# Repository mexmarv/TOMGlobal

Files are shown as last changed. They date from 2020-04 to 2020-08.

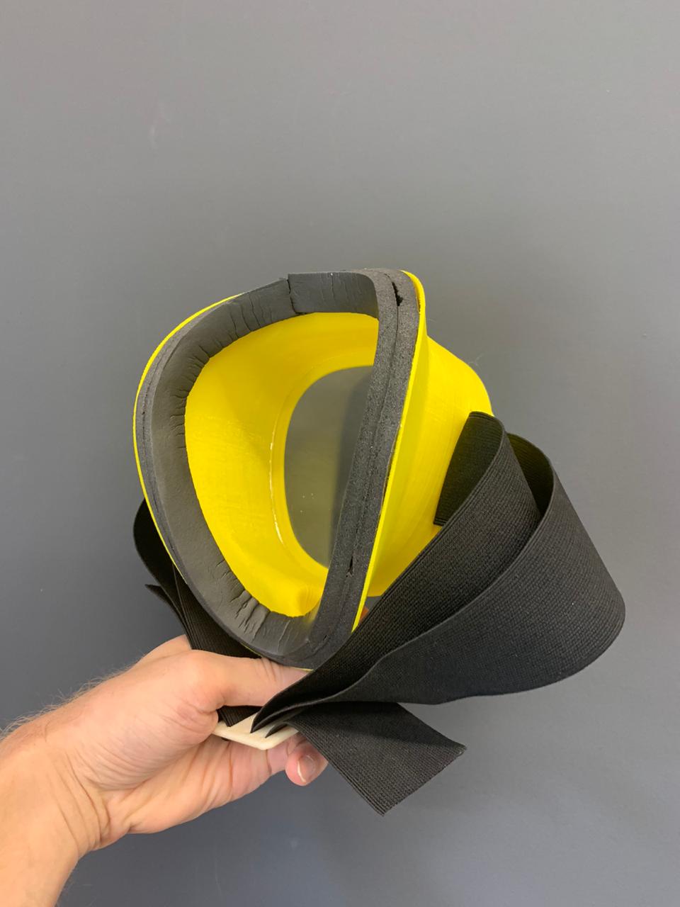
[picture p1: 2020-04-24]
UNO/photos/3.jpeg

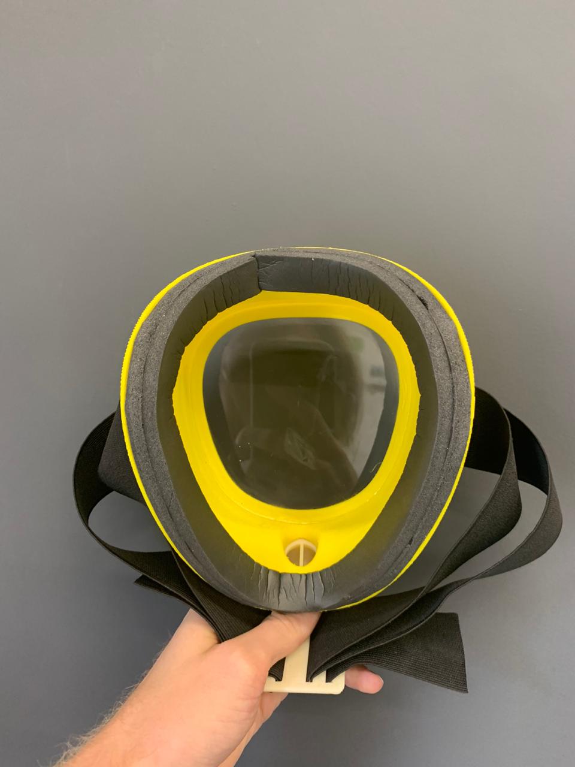
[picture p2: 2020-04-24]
UNO/photos/2.jpeg

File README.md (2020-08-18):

# TOM Global - México Chapter
</br>
<a target="TOM" href="www.makersmexico.org">makersmexico.org</a>

Encuentra todos los archivos de 3D y software que contribuimos de la comunidad que encuentras en makersmexico.org.

## Instalación:
```bash
git clone https://github.com/mexmarv/TOMGlobal.git
cd TOMGlobal
cd .. (UNO | mascaras | splitters | ventiladores)
```
## UNO - Máscara Paciente por ARDS
<li>PEEP-Valve-ARDS_es</li>
<li>UNO *.stl</li>

## mascaras
<li>SitresClips</li>
<li>Stratasys-Letter</li>

## ventiladores
<li>VentMex</li>

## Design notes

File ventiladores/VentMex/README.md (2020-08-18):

# VentMex : Ventilador de Emergencia
</br>
<a target="TOM" href="www.makersmexico.org">makersmexico.org/ventmex</a>

Puedes ver el sitio del proyecto directamente para explicación de todo el proyecto.

## Instalación:
```bash
git clone https://github.com/mexmarv/TOMGlobal.git
cd TOMGlobal/ventiladores/VentMex
cd .. ( VM2.1 | VM-SensorTest | VM-MotorTest | STL | gerber | otros )
```
## VM2.1
<ul>
<li>Software y Libs de Arduino para VentMex
<ul>
<li> Se incluye Librería de encoder del AMS-AS5048B, Nuestras Librerías: VMPresion.h, VMFlujo.h, VMConstantes.h 
</li>
</ul>
</li>
<li>Librerías necesarias que se deben de instalar son:
<ul>
<li>
 AccelStepper (Última Version)
</li>
<li>
 U8g2 (Última Versión)
 </li>
 <li>
SparkFun MAX30101x  (Última Versión)
</li>
</ul>
</ul>

## stl
<li>Archvos Imprimibles de VentMex 2.1 formato .STL</li>
<li>Recomendamos impresión con 80% infill y soportes donde sea necsario</li>

## gerber
<li>Archvos para hacer tu propio VentMex 2.0 Shield para Arduino Mega.</li>

## otros
<li>BOM (Bill of Materials - Lista de Materiales), Cálculo de Volúmen Comandado a pasos, y otros.</li>
<li>Varios</li>

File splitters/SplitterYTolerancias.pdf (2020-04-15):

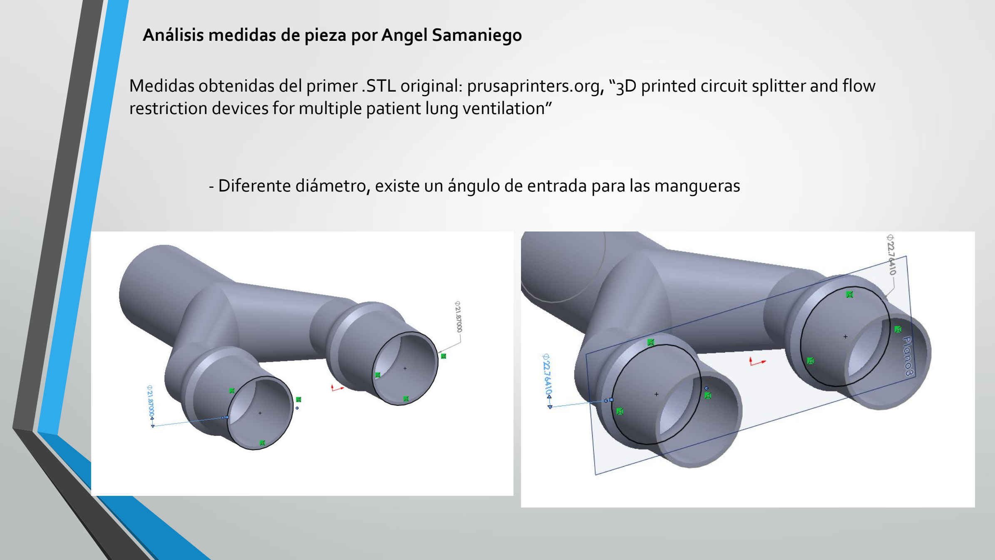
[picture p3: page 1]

Medidas obtenidas del primer .STL original: prusaprinters.org, “3D printed circuit splitter and flow restriction devices for multiple patient lung ventilation”

Análisis medidas de pieza por Angel Samaniego

- Diferente diámetro, existe un ángulo de entrada para las mangueras

Medidas obtenidas del primer STL original:

- Diferente diámetro, existe un Angulo de entrada para las mangueras

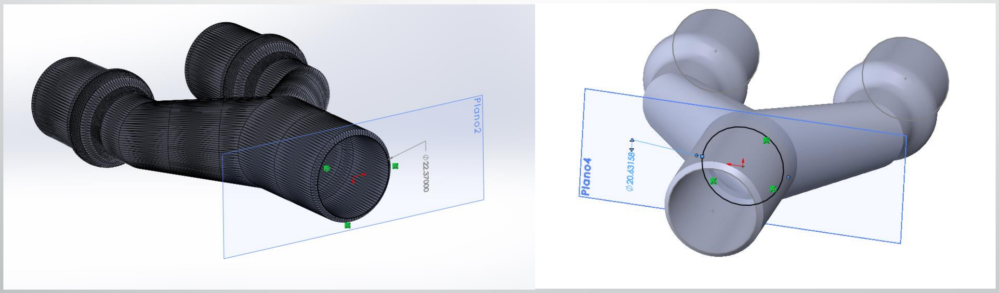
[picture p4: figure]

Tamaño Correcto 22.37 mm

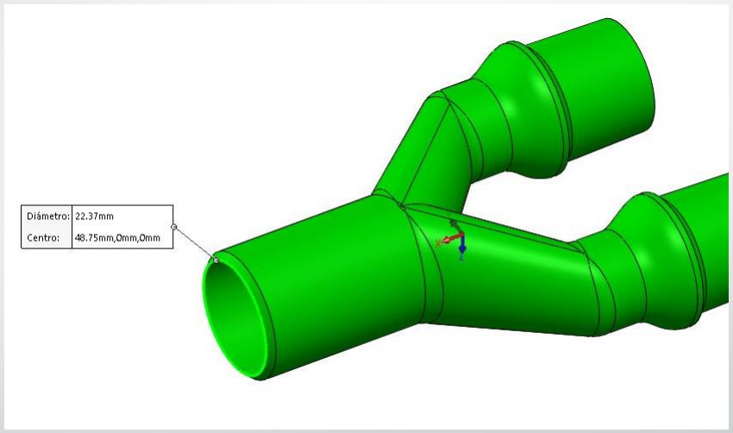
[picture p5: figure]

Tamaño Correcto 21.87 mm

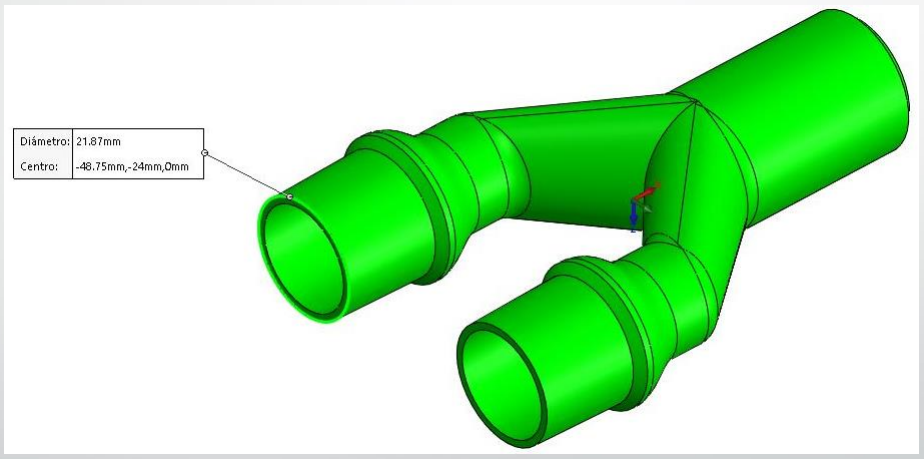
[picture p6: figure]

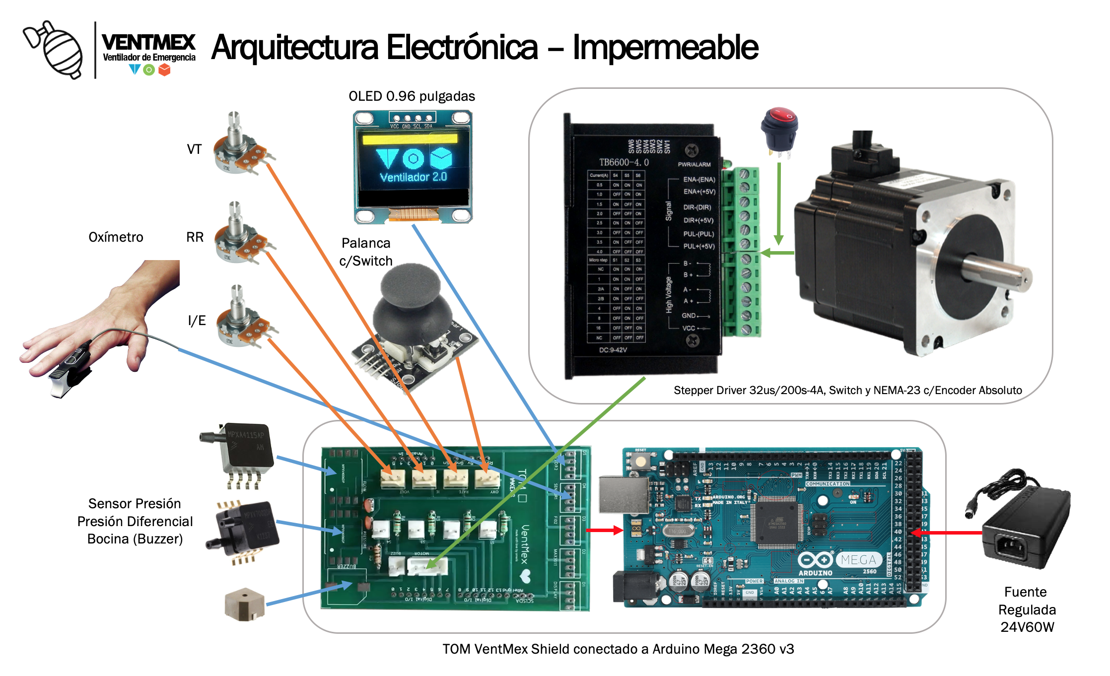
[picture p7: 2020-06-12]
ventiladores/VentMex/otros/VM_DiagElec-figs.png

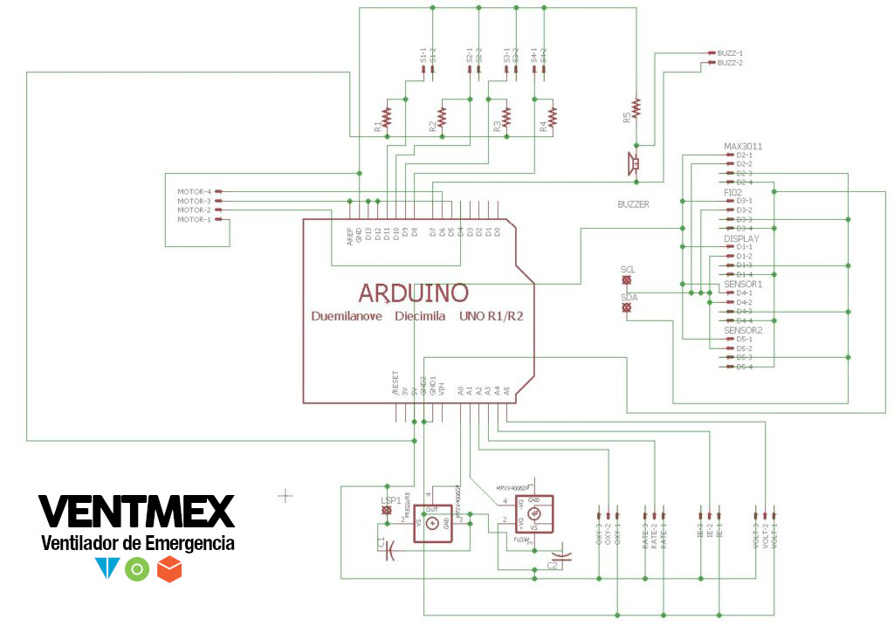
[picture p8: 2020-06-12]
ventiladores/VentMex/otros/VM_DiagElec-schem.jpg

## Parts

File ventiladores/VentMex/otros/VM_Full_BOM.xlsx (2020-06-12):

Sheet: Sheet 1 - VentCore
VentMex - BOM (Bill of Materials) |  |  |  |  |  | Tipo de Cambio | $22.50 | $7889.57
Ca | Familia | Valor | Parte | Paquete | Piezas | Precio USD | Precio MXN | Importe MXN | Comentarios | Imagen
1 | ELECTRONICO | AUDIO MAGNETIC XDCR 3-7V SMD | BUZZER | BUZZ | BUZZ | $1.54 | $34.65 | $34.65
1 | ELECTRONICO | MPXV4006DP | MPXV4006DP | SOP8 | SN1 | $19.55 | $439.88 | $439.88
1 | ELECTRONICO | MPXV4006GP | MPXV4006GP | SOP8 | SN3 | $19.55 | $439.88 | $439.88
5 | ELECTRONICO |  | Resistencia 10k |  | R1, R2, R3, R4 ,R5 | $0.05 | $1.12 | $5.62
2 | ELECTRONICO |  | Resistencia 90 ohms |  | R6 R7 | $0.05 | $1.12 | $2.25
2 | ELECTRONICO |  | Capacitor Ceramico 100 uF |  | C1 y C2 | $0.07 | $1.69 | $3.38
1 | ELECTRONICO |  | Arduino Mega |  |  | $11.11 | $250.00 | $250.00
1 | ELECTRONICO |  | 12V 60W AC/DC Fuente de alimentación |  |  | $20.00 | $450.00 | $450.00
1 | ELECTRONICO |  | Stepper motor Nema-23P |  |  | $38.69 | $870.52 | $870.52
1 | ELECTRONICO |  | Driver TB660 4 A |  |  | $20.89 | $470.00 | $470.00
1 | ELECTRONICO |  | VentMex Shield |  |  | $3.56 | $80.00 | $80.00
3 | ELECTRONICO |  | Potentiometer |  |  | $0.44 | $10.00 | $30.00 | 10 K
1 | ELECTRONICO |  | Conector 12v IP67 |  |  | $9.00 | $202.50 | $202.50
1 | ELECTRONICO |  | SWITCH IP67 |  |  | $2.00 | $45.00 | $45.00
1 | ELECTRONICO |  | Conector USB IP67 para programador |  |  | $15.00 | $337.50 | $337.50
1 | ELECTRONICO |  | Encoder Magnetico |  |  | $16.00 | $360.00 | $360.00
1 | ELECTRONICO |  | Display |  |  | $5.73 | $129.00 | $129.00
1 | ELECTRONICO |  | Oximetro Max30102 |  |  | $10.67 | $240.00 | $240.00
1 | ELECTRONICO |  | Joystick Arduino c/botón |  | Mercado libre | $5.73 | $129.00 | $129.00
1 | MECANICO |  | O_belt |  |  | $1.60 | $36.00 | $36.00
 | MECANICO |  | Baleros 6 |  | MercadoLibre | $2.22 | $50.00 | $50.00
1 | MECANICO | alucobond_file | CNC_bottom |  |  | $15.91 | $358.00 | $358.00 | http://www.dimmaq.com/
1 | MECANICO | sheetmetal_files | SM_internal |  |  | $13.11 | $295.00 | $295.00 | http://www.dimmaq.com/
1 | MECANICO | acrylic_files | CNC_back |  |  | $5.69 | $128.00 | $128.00 | http://www.dimmaq.com/
1 | MECANICO | acrylic_files | CNC_front |  |  | $5.69 | $128.00 | $128.00 | http://www.dimmaq.com/
1 | MECANICO | sheetmetal_files | SM_external |  |  | $10.00 | $225.00 | $225.00 | http://www.dimmaq.com/
1 | MEDICO | Dispositivo de ventilación Bolsa-Válvula-Mascara BVM | BVM v1 |  |  | $31.73 | $714.00 | $714.00
1 | MEDICO |  | Circuito Ventilador Medico 2 Trampas De Agua 1.5m |  | Peso(g) | $26.67 | $600.00 | $600.00 | Mercado Libre (https://articulo.mercadolibre.com.mx/MLM-766206422-circuito-ventilador-medico-2-trampas-de-agua-15m-_JM?quantity=1)
3 | IMPRESION 3D | STL_files | 3PD_spin(rodillo) | Relleno 50%, espesor de capa 0.15 | 45 | $1.20 | $27.00 | $81.00 | Talla 30 x 30 x 50 Volumen ( mm 3 ) 33,677
1 | IMPRESION 3D | STL_files | 3DP_bvmholder_2aP(soporte ambu) | Relleno 100%, espesor de capa 0.15 | 31 | $0.83 | $18.60 | $18.60 | Talla 8 x 88 x 61 Volumen ( mm 3 ) 24,004
3 | IMPRESION 3D | STL_files | 3DP_knobs(potencionmetros) | Relleno 100%, espesor de capa 0.15 | 4 | $0.11 | $2.40 | $7.20 | Talla 18 x 15 x 18 Volumen ( mm 3 ) 2,045
2 | IMPRESION 3D | STL_files | 3DP_pcbholder | Relleno 50%, espesor de capa 0.15 | 2 | $0.05 | $1.20 | $2.40 | Talla 10 x 4 x 35 Volumen ( mm 3 ) 868
1 | IMPRESION 3D | STL_files | 3PD_arc_1 (Bolsa Ambu Bag) | Relleno 35%, espesor de capa 0.15 | 218 | $5.81 | $130.80 | $130.80 | Talla 120 x 40 x 110 Volumen ( mm 3 ) 305,245
1 | IMPRESION 3D | STL_files | 3DP_bvmholder_1aP(soporte ambu) | Relleno 100%, espesor de capa 0.15 | 43 | $1.15 | $25.80 | $25.80 | Talla 8 x 94 x 85 Volumen ( mm 3 ) 33,079
1 | IMPRESION 3D | STL_files | 3DP_bvmholder_1bP(soporte ambu) | Relleno 100%, espesor de capa 0.15 | 22 | $0.59 | $13.20 | $13.20 | Talla 8 x 94 x 85 Volumen ( mm 3 ) 16,719
1 | IMPRESION 3D | STL_files | 3DP_bvmholder_2bP(soporte ambu) | Relleno 100%, espesor de capa 0.15 | 19 | $0.51 | $11.40 | $11.40 | Talla 8 x 88 x 61 Volumen ( mm 3 ) 14,783
1 | IMPRESION 3D | STL_files | 3DP_motor_3(motor) | Relleno 50%, espesor de capa 0.15 | 2 | $0.05 | $1.20 | $1.20 | Talla 5 x 30 x 30 Volumen ( mm 3 ) 1,510
1 | IMPRESION 3D | STL_files | 3DP_motor_1(rodillo ranurado) | Relleno 50%, espesor de capa 0.15 | 45 | $1.20 | $27.00 | $27.00 | Talla 40 x 40 x 59 Volumen ( mm 3 ) 57,388
1 | IMPRESION 3D | STL_files | 3DP_motor_2(motor) | Relleno 50%, espesor de capa 0.15 | 2 | $0.05 | $1.20 | $1.20 | Talla 6 x 33 x 15 Volumen ( mm 3 ) 1,178
3 | SUJECION |  | O_shoulderscrew |  |  | $3.55 | $79.88 | $239.62 | Tornillos de eje de rodamiento - con ranura de anillo de retención, Soporte Sspin Ø6mm (https://www.fastenal.com/)
3 | SUJECION |  | hex nut style 1 gradeab_iso_ISO - 4032 - M6 - D - N |  |  | $1.23 | $27.68 | $83.03 | https://www.fastenal.com/
4 | SUJECION |  | pan head cross recess screw_iso_ISO 7045 - M5 x 10 - Z - 10N |  |  | $0.19 | $4.28 | $17.10 | https://www.fastenal.com/
10 | SUJECION |  | pan head cross recess screw_iso_ISO 7045 - M3 x 10 - Z - 10N |  |  | $0.18 | $4.05 | $40.50 | https://www.fastenal.com/
12 | SUJECION |  | pan head cross recess screw_iso_ISO 7045 - M3 x 12 - Z - 12N |  |  | $0.27 | $6.08 | $72.90 | https://www.fastenal.com/
16 | SUJECION |  | hex nut style 1gradeab_iso_ISO - 4032 - M3 - D - N |  |  | $0.04 | $0.90 | $14.40 | https://www.fastenal.com/
14 | SUJECION |  | pan head cross recess screw_iso_ISO 7045 - M4 x 12 - Z - 12N |  |  | $0.11 | $2.48 | $34.65 | https://www.fastenal.com/
4 | SUJECION |  | hex nut style 1 gradeab_iso_ISO - 4032 - M5 - D - N |  |  | $0.16 | $3.60 | $14.40 | https://www.fastenal.com/

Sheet: Inventory
 |  |  |  |  |  |  | VentCore BOM |  |  | Tipo de Cambio | $24.12 | $7763.70
Qty | Imagen | DigiKey Part Number | Manufacturer Part Number | Description | Familia | Value | Device | Package | Parts | Precio USD | Precio MXN | Importe MXN | Comentarios | Quantity | DigiKey Part Number | Manufacturer Part Number | Description | Customer Reference | Available | Backorder | Unit Price | Extended Price USD
1 |  | 102-1266-1-ND | CT-1205H-SMT-TR | AUDIO MAGNETIC XDCR 3-7V SMD | ELECTRONIC |  | BUZZER | BUZZ | BUZZ | $1.54 | $37.14 | $37.14 |  | 1 | 102-1266-1-ND | CT-1205H-SMT-TR | AUDIO MAGNETIC XDCR 3-7V SMD | BUZZ | 1 | 0 | $1.54
1 |  | KPJX-4S-S | 2092-KPJX-4S-S-ND | CONN JACK FMALE 4POS SOLDADURA DE ESTAÑO | ELECTRONIC |  | KPJX-4S | KPJX-4S | J7 | $2.23 | $53.78 | $53.78 | Remplaza KPJX-4S-S a 2092-KPJX-4S-ND | 1 | KPJX-4S-S | 2092-KPJX-4S-S-ND | CONN JACK FMALE 4POS SOLDADURA DE ESTAÑO |  | 1 | 0 | $2.23
1 |  | 497-12404-ND | L7805CV-DG | IC REG LINEAR 5V 1.5A TO220 | ELECTRONIC |  | L7805CV-DG | TO220-IGO | IC2 | $0.57 | $13.75 | $13.75 |  | 1 | 497-12404-ND | L7805CV-DG | IC REG LINEAR 5V 1.5A TO220 |  | 1 | 0 | $0.57
2 |  | P.10AJCT-ND | ERJ-3RSFR10V | RES 0.1 OHM 1% 1/10W 0603 | ELECTRONIC | 0.1R | 0603 | R0603 | R14, R23 | $0.29 | $6.99 | $13.99 |  | 2 | P.10AJCT-ND | ERJ-3RSFR10V | RES 0.1 OHM 1% 1/10W 0603 |  | 2 | 0 | $0.29
1 |  | RHM100DCT-ND | ESR03EZPJ101 | RES SMD 100 OHM 5% 1/4W 0603 | ELECTRONIC | 100R | 0603 | R0603 | R7 | $0.10 | $2.41 | $2.41 |  | 1 | RHM100DCT-ND | ESR03EZPJ101 | RES SMD 100 OHM 5% 1/4W 0603 |  | 1 | 0 | $0.10
11 |  | 399-1100-1-ND | C0603C104Z3VACTU | CAP CER 0.1UF 25V Y5V 0603 | ELECTRONIC | 100nF | 0603 | C0603 | C17, C22, C25, C27, C33, C10, C11, C4, C5, C6, C8 | $0.03 | $0.77 | $8.49 | Faltan en BOM Ruben |  | 399-1100-1-ND | C0603C104Z3VACTU | CAP CER 0.1UF 25V Y5V 0603 |  | 11 | 0 | $0.03
6 |  | 718-1920-1-ND | TL8A0107M6R3C | Vishay Sprague | ELECTRONIC | 100uF | C-PR-SMD-SV-D | SV-D | C15 | $1.36 | $32.80 | $196.78 | Faltan en BOM Ruben |  | 718-1920-1-ND | TL8A0107M6R3C | Vishay Sprague | CAP TANT 100UF 20% 6.3V 1206 | 6 | 0 | $1.36
2 |  | 311-10KGRCT-ND | RC0603JR-0710KL | RES SMD 10K OHM 5% 1/10W 0603 | ELECTRONIC | 10K | 0603 | R0603 | R1, R4, R5, R6, R8, R21 | $0.19 | $4.58 | $9.16 |  | 10 | 311-10KGRCT-ND | RC0603JR-0710KL | RES SMD 10K OHM 5% 1/10W 0603 | R1, R4, R5, R6, R8, R21 | 10 | 0 | $19.00
6 |  | TC33X-103ECT-ND | TC33X-2-103E | TRIMMER 10K OHM 0.1W J LEAD TOP | ELECTRONIC | 10k | TRIMPOTTC33X | TC33X | VR1 | $0.28 | $6.75 | $40.51 |  | 1 | TC33X-103ECT-ND | TC33X-2-103E | TRIMMER 10K OHM 0.1W J LEAD TOP |  | 1 | 0 | $0.28
1 |  | 399-7842-1-ND | C0603C103M5RACTU | CAP CER 10000PF 50V X7R 0603 | ELECTRONIC | 10nF | 0603 | C0603 | C19 | $0.10 | $2.41 | $2.41 |  | 1 | 399-7842-1-ND | C0603C103M5RACTU | CAP CER 10000PF 50V X7R 0603 |  | 1 | 0 | $0.10
1 |  | 718-1124-1-ND | 293D106X9016B2TE3 | Vishay Sprague | ELECTRONIC | 10uF | C-PR-SMD-SV-B | SV-B | C16 | $0.44 | $10.61 | $10.61 | Faltan en BOM Ruben |  | 718-1124-1-ND | 293D106X9016B2TE3 | Vishay Sprague | CAP TANT 10UF 10% 16V 1411 | 6 | 0 | $0.44
1 |  | 399-4925-1-ND | C0805C106K8PACTU | CAP CER 10UF 10V X5R 0805 | ELECTRONIC | 10uf | 0805 | C0805 | C9 | $0.16 | $3.86 | $3.86 |  | 1 | 399-4925-1-ND | C0805C106K8PACTU | CAP CER 10UF 10V X5R 0805 |  | 1 | 0 | $0.16
1 |  | 311-120ARCT-ND | RC0805JR-07120RL | RES SMD 120 OHM 5% 1/8W 0805 | ELECTRONIC | 120R | 0805 | R0805 | R36 | $0.10 | $2.41 | $2.41 |  | 1 | 311-120ARCT-ND | RC0805JR-07120RL | RES SMD 120 OHM 5% 1/8W 0805 |  | 1 | 0 | $0.10
1 |  | 535-9875-1-ND | ABLS2-16.000MHZ-D4Y-T | CRYSTAL 16.0000MHZ 18PF SMD | ELECTRONIC | 16MHZ | DIP-CRYSTAL-16MHZ-18PF-30PPM-40R(HC49US) | HC49US | Y1 | $0.46 | $11.09 | $11.09 |  | 1 | 535-9875-1-ND | ABLS2-16.000MHZ-D4Y-T | CRYSTAL 16.0000MHZ 18PF SMD |  | 1 | 0 | $0.46
1 |  | 1N4004-TPMSCT-ND | 1N4004-TP | DIODE GEN PURP 400V 1A DO41 | ELECTRONIC | 1N4004 | 1N4004 | DO41-10 | D1 | $0.12 | $2.89 | $2.89 |  | 1 | 1N4004-TPMSCT-ND | 1N4004-TP | DIODE GEN PURP 400V 1A DO41 |  | 1 | 0 | $0.12
2 |  | 1276-6524-1-ND | CL10B105MO8NNWC | TAPA CER 1UF 16V X7R 0603 | ELECTRONIC | 1uf | 0603 | C0603 | C3, C7 | $0.10 | $2.41 | $4.82 | Review vs partida 19 399-3118-1-ND C0603C105K8PACTU | 2 | 1276-6524-1-ND | CL10B105MO8NNWC | TAPA CER 1UF 16V X7R 0603 | C3, C7 | 2 | 0 | $0.10
2 |  | 311-22.0HRCT-ND | RC0603FR-0722RL | RES SMD 22 OHM 1% 1/10W 0603 | ELECTRONIC | 22R | 0603 | R0603 | R2, R3 | $0.10 | $2.41 | $4.82 |  | 2 | 311-22.0HRCT-ND | RC0603FR-0722RL | RES SMD 22 OHM 1% 1/10W 0603 |  | 2 | 0 | $0.10
2 |  | 399-7874-1-ND | C0603C220J1GACTU | CAP CER 22PF 100V C0G/NP0 0603 | ELECTRONIC | 22pf | 0603 | C0603 | C1, C2 | $0.10 | $2.41 | $4.82 |  | 2 | 399-7874-1-ND | C0603C220J1GACTU | CAP CER 22PF 100V C0G/NP0 0603 |  | 2 | 0 | $0.10
1 |  | 311-3365-1-ND | CC0603KRX5R8BB474 | CAP CER 0.47UF 25V X5R 0603 | ELECTRONIC | 470nF | 0603 | C0603 | C23 | $0.18 | $4.34 | $4.34 |  | 1 | 311-3365-1-ND | CC0603KRX5R8BB474 | CAP CER 0.47UF 25V X5R 0603 |  | 1 | 0 | $0.18
1 |  | ATMEGA32U4-AU-ND | ATMEGA32U4-AU | IC MCU 8BIT 32KB FLASH 44TQFP | ELECTRONIC | ATMEGA32U4-TQFP44 | MCU-ATMEGA32U4-AU(TQFP44) | TQFP44-0.8-9.6X9.6MM | U1 | $4.00 | $96.46 | $96.46 |  | 1 | ATMEGA32U4-AU-ND | ATMEGA32U4-AU | IC MCU 8BIT 32KB FLASH 44TQFP | U1 | 1 | 0 | $4.00
1 |  | 609-2845-ND | 75869-131LF | CONN HEADER VERT 6POS 2.54MM | ELECTRONIC | 2x3 2.54mm Male Header | 2x3 2.54mm Male Header | 2x3 2.54mm Male Header | ISP1 | $0.77 | $18.57 | $18.57 |  | 1 | 609-2845-ND | 75869-131LF | CONN HEADER VERT 6POS 2.54MM | ISP1 | 1 | 0 | $0.77
1 |  | 490-5988-1-ND | BLM21PG331SN1D | FERRITE BEAD 330 OHM 0805 1LN | ELECTRONIC | BLM21PG331SN1D | 0805 | R0805 | FERRITE | $0.11 | $2.65 | $2.65 |  | 1 | 490-5988-1-ND | BLM21PG331SN1D | FERRITE BEAD 330 OHM 0805 1LN |  | 1 | 0 | $0.11
1 |  | 296-28915-5-ND | DRV8825PWP | IC MTR DRVR BIPLR 8.2-45V 28SSOP | ELECTRONIC | DRV8825PWP | DRV8825PWP | TSSOP-28 | U4 | $5.09 | $122.75 | $122.75 |  | 1 | 296-28915-5-ND | DRV8825PWP | IC MTR DRVR BIPLR 8.2-45V 28SSOP | U4 | 1 | 0 | $5.09
1 |  | 455-1734-1-ND | B2B-PH-SM4-TB(LF)(SN) | CONN HEADER SMD 2POS 2MM | ELECTRONIC | JST-PH_2-PIN_HEADER | JST-PH_2-PIN_HEADER (90 DEG) | JST_B2B-PH_HEADER | J1 | $0.55 | $13.26 | $13.26 |  | 1 | 455-1734-1-ND | B2B-PH-SM4-TB(LF)(SN) | CONN HEADER SMD 2POS 2MM | J1 | 1 | 0 | $0.55
4 |  | 455-1817-ND | B02B-PASK (LF) (SN) | CONN HEADER VERT 2POS 2MM | ELECTRONIC | JST-PH_2-PIN_HEADER | JST-PH_2-PIN_HEADER | JST_B2B-PH_HEADER | J3, J6, J9, J11 | $0.25 | $6.03 | $24.12 | Review vs partida 6 | 4 | 455-1817-ND | B02B-PASK (LF) (SN) | CONN HEADER VERT 2POS 2MM | J3, J6, J9, J11 | 4 | 0 | $0.25
4 |  | 455-1705-ND | B3B-PH-K-S(LF)(SN) | CONN HEADER VERT 3POS 2MM | ELECTRONIC | JST-PH_3-PIN_HEADER | JST-PH_3-PIN_HEADER | JST_B3B-PH_HEADER | J2, J4, J5, J8 | $0.19 | $4.58 | $18.33 |  | 4 | 455-1705-ND | B3B-PH-K-S(LF)(SN) | CONN HEADER VERT 3POS 2MM | J2, J4, J5, J8 | 4 | 0 | $0.19
1 |  | 455-1721-ND | S4B-PH-K-S(LF)(SN) | CONN HEADER R/A 4POS 2MM | ELECTRONIC | JST-PH_4-PIN_HEADER | JST-PH_4-PIN_HEADER (90DEG) | JST_B4B-PH_HEADER | J10 | $0.22 | $5.31 | $5.31 |  | 1 | 455-1721-ND | S4B-PH-K-S(LF)(SN) | CONN HEADER R/A 4POS 2MM | J10 | 1 | 0 | $0.22
1 |  | MPXV4006DP-ND | MPXV4006DP | SENSOR PRESSURE DUAL SMD 8-SOP | ELECTRONIC | MPXV4006DP | MPXV4006DP | SOP8 | SN1 | $19.55 | $471.46 | $471.46 |  | 1 | MPXV4006DP-ND | MPXV4006DP | SENSOR PRESSURE DUAL SMD 8-SOP | SN1 | 1 | 0 | $19.55
1 |  | MPXV4006GP-ND | MPXV4006GP | SENSOR GAUGE PRESS .87PSI MAX | ELECTRONIC | MPXV4006GP | MPXV4006GP | SOP8 | SN3 | $19.55 | $471.46 | $471.46 |  | 1 | MPXV4006GP-ND | MPXV4006GP | SENSOR GAUGE PRESS .87PSI MAX | SN3 | 1 | 0 | $19.55
1 |  | 475-1415-1-ND | LH R974-LP-1 | LED RED DIFFUSED 0805 SMD | ELECTRONIC | RED-0805 | 0805 | LED-0805 | D3 | $0.19 | $4.61 | $4.61 | *** Falta en BOM Ruben | 1 | 475-1415-1-ND | LH R974-LP-1 | LED RED DIFFUSED 0805 SMD |  | 1 | 0 | $0.19
1 |  | AE11183-ND | AU-Y1007 | Assmann WSW Components | ELECTRONIC | USB+SHIELD | USB+SHIELD | USB-B-PTH | U2 | $0.73 | $17.60 | $17.60 | Remplaza 33UBBBR-04SW11 por AU-Y1007 Assmann WSW Components | 1 | AE11183-ND | AU-Y1007 | Assmann WSW Components | CONN RCPT USB1.1 TYPEB 4POS R / A | 1 | 0 | $0.73
2 |  | EG2350-ND | 100SP1T1B1M1QEH | E-Switch | ELECTRONIC |  | Toggle Switch |  |  | $1.92 | $46.30 | $92.60 |  |  | EG2350-ND | 100SP1T1B1M1QEH | E-Switch | INTERRUPTOR DE CAMBIO SPDT 5A 120V | 2 | 0 | $1.92
1 |  | SW986-ND | SS-5GL | Omron Electronics Inc-EMC Div | ELECTRONIC |  | OMRON SS-5GL P |  |  | $1.88 | $45.34 | $45.34 |  |  | SW986-ND | SS-5GL | Omron Electronics Inc-EMC Div | INTERRUPTOR SNAP ACTION SPDT 5A 125V | 1 | 0 | $1.88
1 |  | 1568-1376-ND | ROB-13656 | STEP MOTOR HYBRID BIPOLAR 3.2V | ELECTRONIC |  | Stepper motor Nema-23P |  |  | $38.69 | $933.03 | $933.03 |  | 1 | 1568-1376-ND | ROB-13656 | STEP MOTOR HYBRID BIPOLAR 3.2V | NEMA 23 | 1 | 0 | $38.69
1 |  |  |  |  | ELECTRONIC |  | PCB |  |  | $2.07 | $50.00 | $50.00
3 |  | CT2153-ND | 026TB32R500B1A1 | Electrocomponentes CTS | ELECTRONIC |  | Potentiometer |  |  | $5.24 | $126.37 | $379.10 | Revisar Valores antes |  | CT2153-ND | 026TB32R500B1A1 | Electrocomponentes CTS | POT 50 OHM 5W ALAMBRE LINEAL | 3 | 0 | $5.24
1 |  |  |  | O_belt | MECHANICAL |  | O_belt |  |  | $1.49 | $36.00 | $36.00 | #VALUE! (https://articulo.mercadolibre.com.mx/MLM-756286284-epman-rollo-10m-cinturon-seguridad-automotriz-_JM?matt_tool=35355233&matt_word&quantity=1&variation=503849)
1 |  |  |  | CNC_bottom | MECHANICAL | alucobond_file | CNC_bottom |  |  | $20.73 | $500.00 | $500.00 | http://www.dimmaq.com/
1 |  |  |  | SM_internal | MECHANICAL | sheetmetal_files | SM_internal |  |  | $12.23 | $295.00 | $295.00 | http://www.dimmaq.com/
1 |  |  |  | CNC_back | MECHANICAL | acrylic_files | CNC_back |  |  | $10.37 | $250.00 | $250.00 | http://www.dimmaq.com/
1 |  |  |  | CNC_front | MECHANICAL | acrylic_files | CNC_front |  |  | $10.37 | $250.00 | $250.00 | http://www.dimmaq.com/
1 |  |  |  | SM_external | MECHANICAL | sheetmetal_files | SM_external |  |  | $12.23 | $295.00 | $295.00 | http://www.dimmaq.com/
1 |  |  |  | Set de Etiquetas Controles | GRAPHICS |  | Set de Etiquetas Controles |  |  | $0.66 | $16.00 | $16.00 | Etiqueta Volumen Tidal
1 |  |  |  | BVM v1 | MEDICAL | Dispositivo de ventilación Bolsa-Válvula-Mascara BVM | BVM v1 |  |  | $29.61 | $714.00 | $714.00
1 |  |  |  | Circuito Ventilador Medico 2 Trampas De Agua 1.5m | MEDICAL |  | Circuito Ventilador Medico 2 Trampas De Agua 1.5m |  | Peso(g) | $24.88 | $600.00 | $600.00 | Mercado Libre (https://articulo.mercadolibre.com.mx/MLM-766206422-circuito-ventilador-medico-2-trampas-de-agua-15m-_JM?quantity=1)
3 |  |  |  | 3PD_spin(rodillo) | IMPRESION 3D | STL_files | 3PD_spin(rodillo) | Relleno 50%, espesor de capa 0.15 | 45 | $1.12 | $27.00 | $81.00 | Talla 30 x 30 x 50 Volumen ( mm 3 ) 33,677
1 |  |  |  | 3DP_bvmholder_2aP(soporte ambu) | IMPRESION 3D | STL_files | 3DP_bvmholder_2aP(soporte ambu) | Relleno 100%, espesor de capa 0.15 | 31 | $0.77 | $18.60 | $18.60 | Talla 8 x 88 x 61 Volumen ( mm 3 ) 24,004
3 |  |  |  | 3DP_knobs(potencionmetros) | IMPRESION 3D | STL_files | 3DP_knobs(potencionmetros) | Relleno 100%, espesor de capa 0.15 | 4 | $0.10 | $2.40 | $7.20 | Talla 18 x 15 x 18 Volumen ( mm 3 ) 2,045
2 |  |  |  | 3DP_pcbholder | IMPRESION 3D | STL_files | 3DP_pcbholder | Relleno 50%, espesor de capa 0.15 | 2 | $0.05 | $1.20 | $2.40 | Talla 10 x 4 x 35 Volumen ( mm 3 ) 868
1 |  |  |  | 3PD_arc_1 (Bolsa Ambu Bag) | IMPRESION 3D | STL_files | 3PD_arc_1 (Bolsa Ambu Bag) | Relleno 35%, espesor de capa 0.15 | 218 | $5.42 | $130.80 | $130.80 | Talla 120 x 40 x 110 Volumen ( mm 3 ) 305,245
1 |  |  |  | 3DP_bvmholder_1aP(soporte ambu) | IMPRESION 3D | STL_files | 3DP_bvmholder_1aP(soporte ambu) | Relleno 100%, espesor de capa 0.15 | 43 | $1.07 | $25.80 | $25.80 | Talla 8 x 94 x 85 Volumen ( mm 3 ) 33,079
1 |  |  |  | 3DP_bvmholder_1bP(soporte ambu) | IMPRESION 3D | STL_files | 3DP_bvmholder_1bP(soporte ambu) | Relleno 100%, espesor de capa 0.15 | 22 | $0.55 | $13.20 | $13.20 | Talla 8 x 94 x 85 Volumen ( mm 3 ) 16,719
1 |  |  |  | 3DP_bvmholder_2bP(soporte ambu) | IMPRESION 3D | STL_files | 3DP_bvmholder_2bP(soporte ambu) | Relleno 100%, espesor de capa 0.15 | 19 | $0.47 | $11.40 | $11.40 | Talla 8 x 88 x 61 Volumen ( mm 3 ) 14,783
1 |  |  |  | 3DP_motor_3(motor) | IMPRESION 3D | STL_files | 3DP_motor_3(motor) | Relleno 50%, espesor de capa 0.15 | 2 | $0.05 | $1.20 | $1.20 | Talla 5 x 30 x 30 Volumen ( mm 3 ) 1,510
1 |  |  |  | 3DP_motor_1(rodillo ranurado) | IMPRESION 3D | STL_files | 3DP_motor_1(rodillo ranurado) | Relleno 50%, espesor de capa 0.15 | 45 | $1.12 | $27.00 | $27.00 | Talla 40 x 40 x 59 Volumen ( mm 3 ) 57,388
1 |  |  |  | 3DP_motor_2(motor) | IMPRESION 3D | STL_files | 3DP_motor_2(motor) | Relleno 50%, espesor de capa 0.15 | 2 | $0.05 | $1.20 | $1.20 | Talla 6 x 33 x 15 Volumen ( mm 3 ) 1,178 | Descripción |  | Cantidad / paquete | Cantidad ext. | Mayoreo
3 |  | MS2550075A20000 |  | O_shoulderscrew | SUJECION |  | O_shoulderscrew |  |  | $3.55 | $85.61 | $256.83 | Tornillos de eje de rodamiento - con ranura de anillo de retención, Soporte Sspin Ø6mm (https://www.fastenal.com/) | Tornillo de cabeza hueca de acero inoxidable M6-1.0 x 75 mm ISO 4762 / DIN 912 hexagonal A2-70 | SKU: MS2550075A20000 | 1 | 3 | $3.55
3 |  | MN2550000A48000 |  | hex nut style 1 gradeab_iso_ISO - 4032 - M6 - D - N | SUJECION |  | hex nut style 1 gradeab_iso_ISO - 4032 - M6 - D - N |  |  | $1.23 | $29.66 | $88.99 | https://www.fastenal.com/ | M6-1.0 DIN 934 Acabado Acero inoxidable A4 Tuerca hexagonal | SKU: MN2550000A48000 | 1 | 3 | $1.23
4 |  | QM2540008A20000 |  | pan head cross recess screw_iso_ISO 7045 - M5 x 10 - Z - 10N | SUJECION |  | pan head cross recess screw_iso_ISO 7045 - M5 x 10 - Z - 10N |  |  | $0.19 | $4.58 | $18.33 | https://www.fastenal.com/ | M5-0.8 x 8 mm DIN 7985 Phillips Drive Pan Head Tornillo de máquina de acero inoxidable de grado A2 | SKU: QM2540008A20000 | 1 | 4 | $0.19
10 |  | QM2510010A40000 |  | pan head cross recess screw_iso_ISO 7045 - M3 x 10 - Z - 10N | SUJECION |  | pan head cross recess screw_iso_ISO 7045 - M3 x 10 - Z - 10N |  |  | $0.18 | $4.34 | $43.41 | https://www.fastenal.com/ | M3-0.5 x 10 mm DIN 7985 Phillips Drive Pan Head Tornillo de máquina de acero inoxidable de grado A4 | SKU: QM2510010A40000 | 1 | 10 | $0.18
12 |  | QM2510012A40000 |  | pan head cross recess screw_iso_ISO 7045 - M3 x 12 - Z - 12N | SUJECION |  | pan head cross recess screw_iso_ISO 7045 - M3 x 12 - Z - 12N |  |  | $0.27 | $6.51 | $78.13 | https://www.fastenal.com/ | M3-0.5 x 12 mm DIN 7985 Phillips Drive Pan Head Tornillo de máquina de acero inoxidable de grado A4 | SKU: QM2510012A40000 | 1 | 12 | $0.27
16 |  | MN2510000A40000 |  | hex nut style 1gradeab_iso_ISO - 4032 - M3 - D - N | SUJECION |  | hex nut style 1gradeab_iso_ISO - 4032 - M3 - D - N |  |  | $0.04 | $0.96 | $15.43 | https://www.fastenal.com/ | M3-0.5 DIN 934 Acabado Acero inoxidable A4 Tuerca hexagonal | SKU: MN2510000A40000 | 1 | 16 | $0.04
14 |  | QM2530012A20000 |  | pan head cross recess screw_iso_ISO 7045 - M4 x 12 - Z - 12N | SUJECION |  | pan head cross recess screw_iso_ISO 7045 - M4 x 12 - Z - 12N |  |  | $0.11 | $2.65 | $37.14 | https://www.fastenal.com/ | M4-0.7 x 12 mm DIN 7985 Phillips Drive Pan Head Tornillo de máquina de acero inoxidable de grado A2 | SKU: QM2530012A20000 | 1 | 14 | $0.11
4 |  | MN2540000A40000 |  | hex nut style 1 gradeab_iso_ISO - 4032 - M5 - D - N | SUJECION |  | hex nut style 1 gradeab_iso_ISO - 4032 - M5 - D - N |  |  | $0.16 | $3.86 | $15.43 | https://www.fastenal.com/ | M5-0.8 DIN 934 Acabado Acero inoxidable A4 Tuerca hexagonal | SKU: MN2540000A40000 | 1 | 4 | $0.16
1 |  |  |  | Impuestos de Importacion de Componenetes | IMPUESTOS |  | Impuestos de Importacion de Componenetes |  |  | $30.66 | $739.47 | $739.47
 |  |  |  | Ensamble de Componentes en PCBoard |  |  | Ensamble de Componentes en PCBoard

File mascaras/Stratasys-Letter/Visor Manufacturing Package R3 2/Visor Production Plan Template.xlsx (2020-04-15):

 | F370 Day | F370 Night | F450 Day | F450 Night | F900 Day | F900 Night
Time | 2h 11m | 11h 53m | 2h 11m | 11h 39m | 8h 4 m | 11h 44m
Model | 2.663 | 10.093 | 4.42 | 14.109 | 16.262 | 23.649
Support | 1.302 | 11.738 | 0.961 | 11.445 | 3.449 | 5.012
Part Count | 2 | 6 | 3 | 8 | 11 | 16
Runs per day | 3 | 1 | 3 | 1 | 1 | 1
Daily part total per machine | 6 | 6 | 9 | 8 | 11 | 16
Machine Count | 0 | 0 | 0 | 0 | 0 | 0 | Total
Gross Production (single units) | 0 | 0 | 0 | 0 | 0 | 0 | 0
Daily Model Material Use | 0 | 0 | 0 | 0 | 0 | 0 | 0
Daily Support Material Use | 0 | 0 | 0 | 0 | 0 | 0 | 0
Notes: | The print time and material consumption are estimates from GrabCAD Print, actual results may vary.

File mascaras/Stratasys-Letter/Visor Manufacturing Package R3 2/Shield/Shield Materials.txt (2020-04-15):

Stratasys is procuring shields with .04” PETG or our build sheets (P/N  355-00100) that are 0.02” Polycarb.

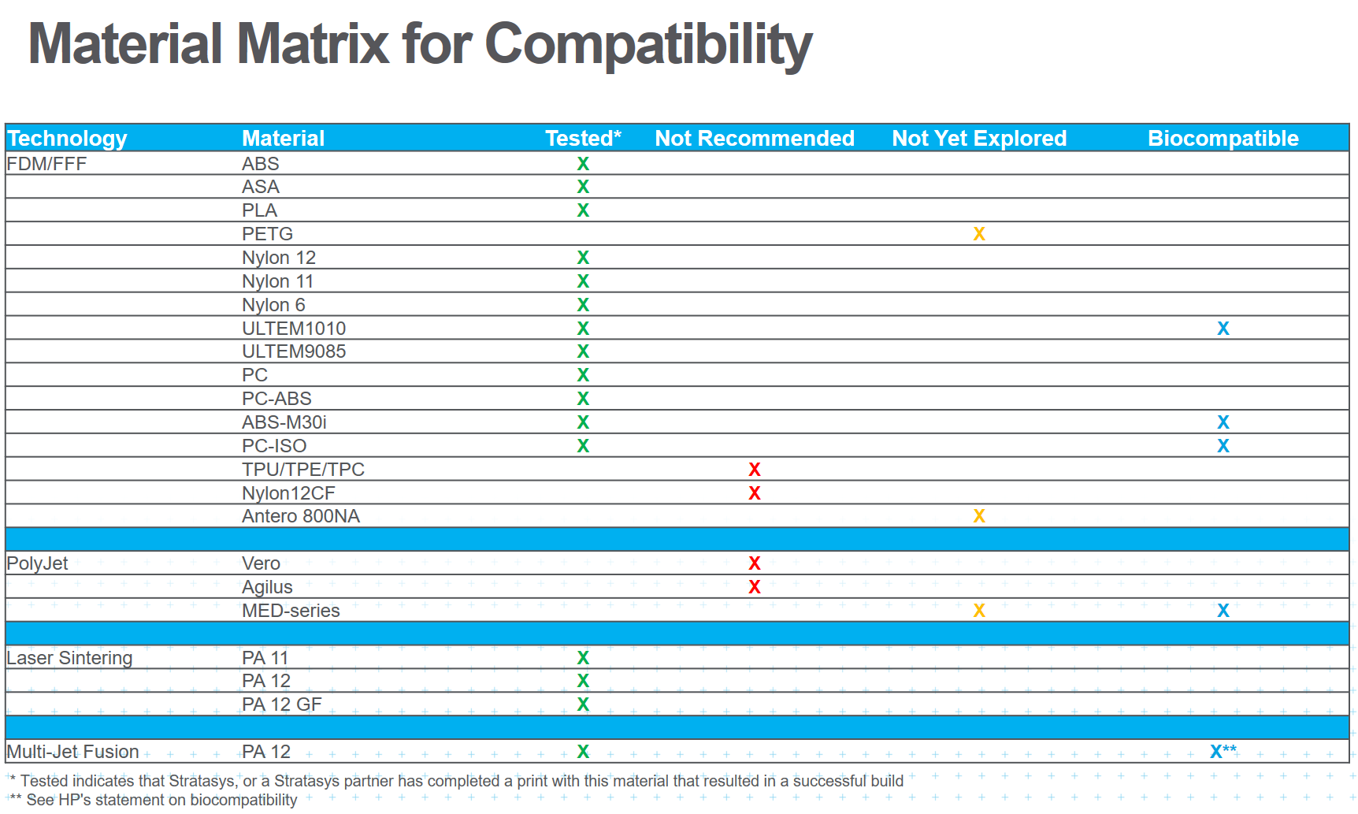
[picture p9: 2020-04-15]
mascaras/Stratasys-Letter/Visor Manufacturing Package R3 2/Material Matrix.PNG

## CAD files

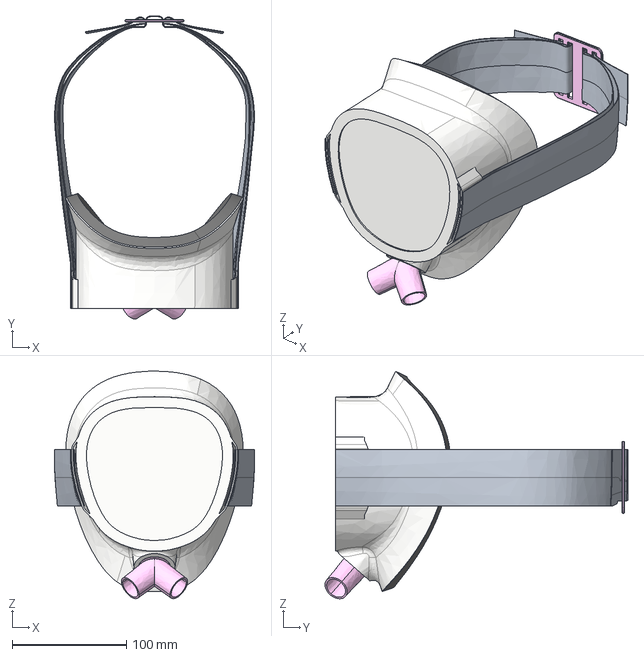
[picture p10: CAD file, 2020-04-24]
UNO/UNO_Complete.stp
174.9 x 264.7 x 198.8 mm

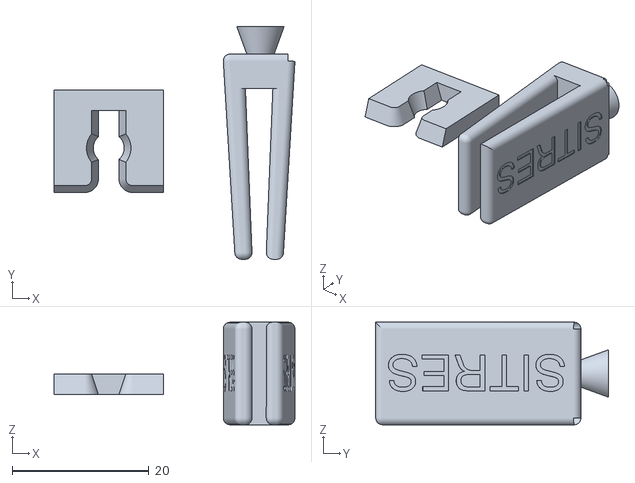
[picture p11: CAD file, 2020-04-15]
mascaras/SitresClips/Gorra.stl
35.2 x 34.0 x 15.0

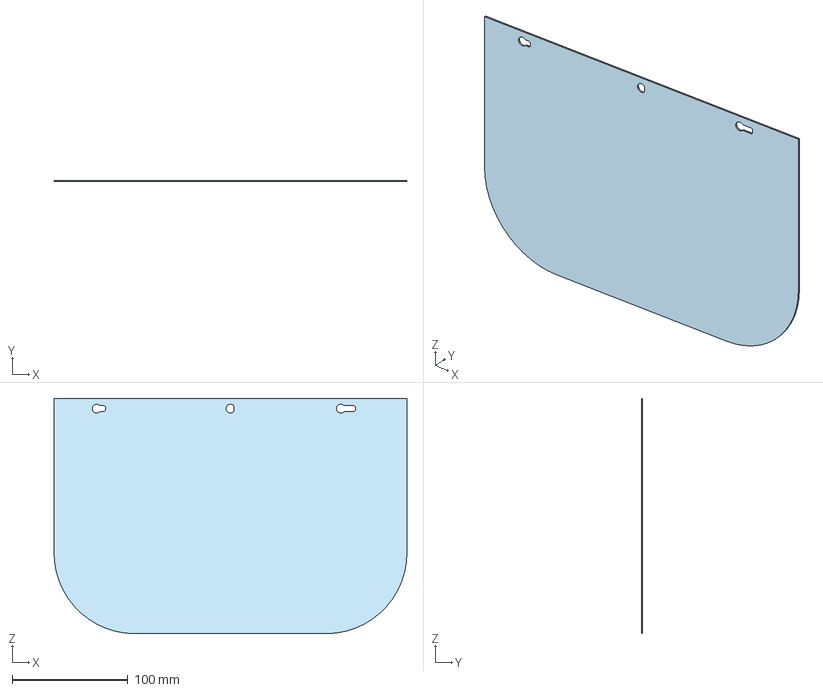
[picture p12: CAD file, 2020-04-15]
mascaras/Stratasys-Letter/Visor Manufacturing Package R3 2/Shield/Shield R2.step
304.8 x 1.27 x 203.2 mm

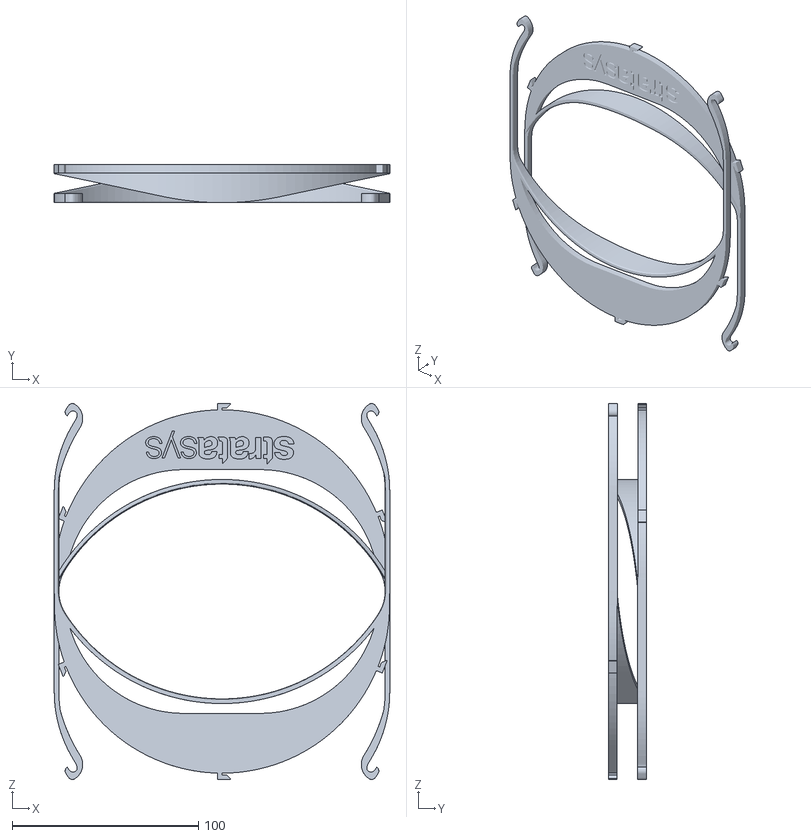
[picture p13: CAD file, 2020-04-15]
mascaras/Stratasys-Letter/Visor Manufacturing Package R3 2/Visor/2-Stack Visor Comfort Release.stl
180.0 x 20.5 x 201.7

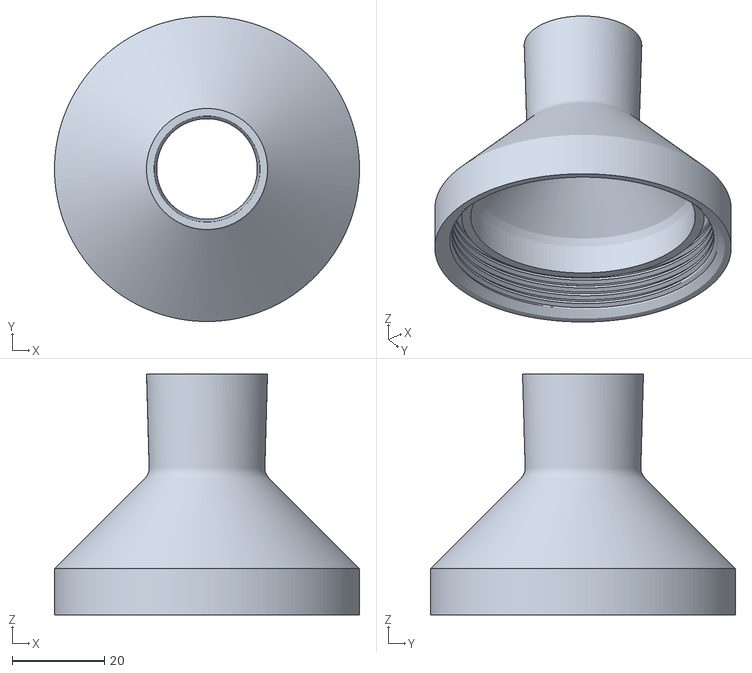
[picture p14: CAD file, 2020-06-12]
splitters/porta filtro hembra v22.stl
66.0 x 66.0 x 52.1

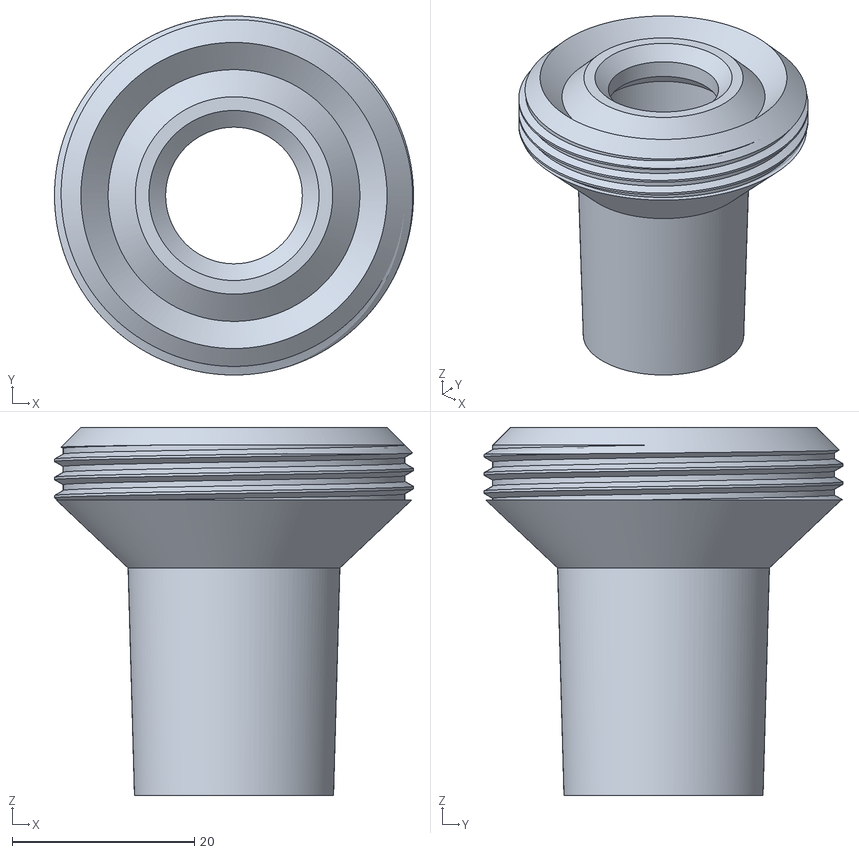
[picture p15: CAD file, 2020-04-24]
UNO/PEEP-Valve-ARDS_es/PEEP_Base.stl
39.4 x 39.4 x 40.4

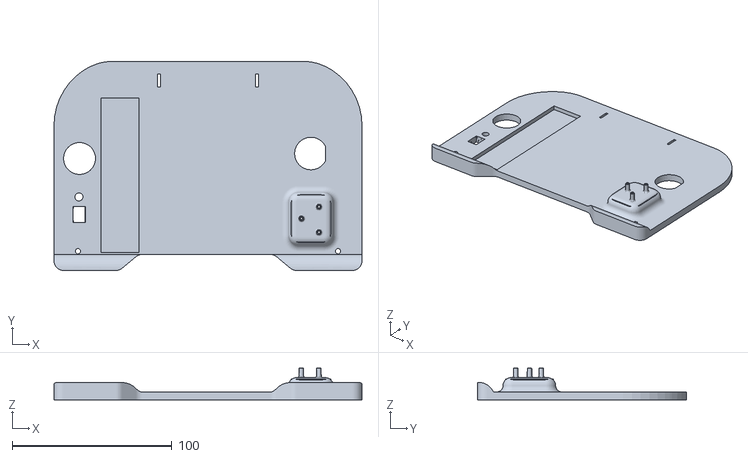
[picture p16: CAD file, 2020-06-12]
ventiladores/VentMex/stl/estructura/TapaTrasera-Ventmex.STL
193.0 x 131.0 x 20.0

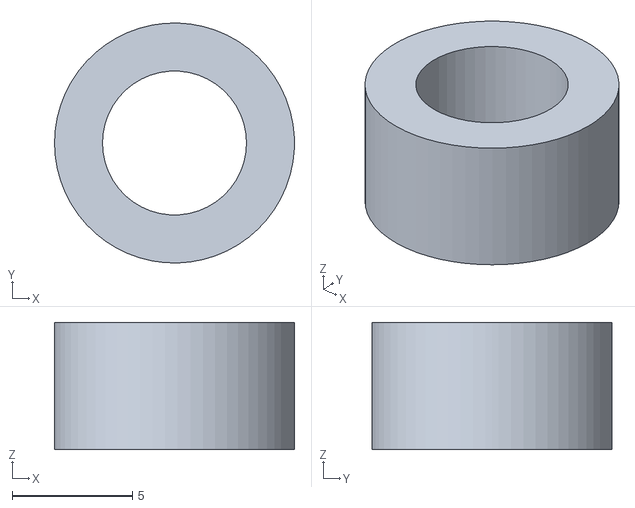
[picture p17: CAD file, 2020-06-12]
ventiladores/VentMex/stl/mecanico/SeparadorParaRodillo-VentMex.STL
10.0 x 10.00 x 5.30

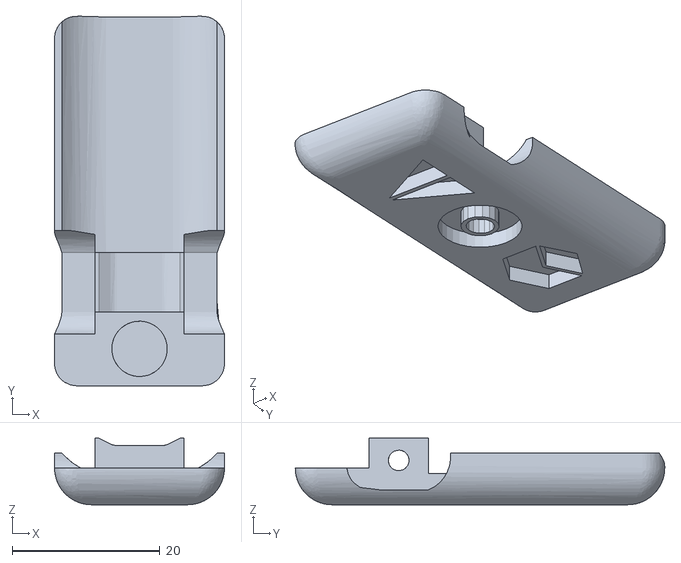
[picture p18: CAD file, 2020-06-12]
ventiladores/VentMex/stl/oximetro/OximetroB-TOM.stl
23.0 x 50.0 x 9.00

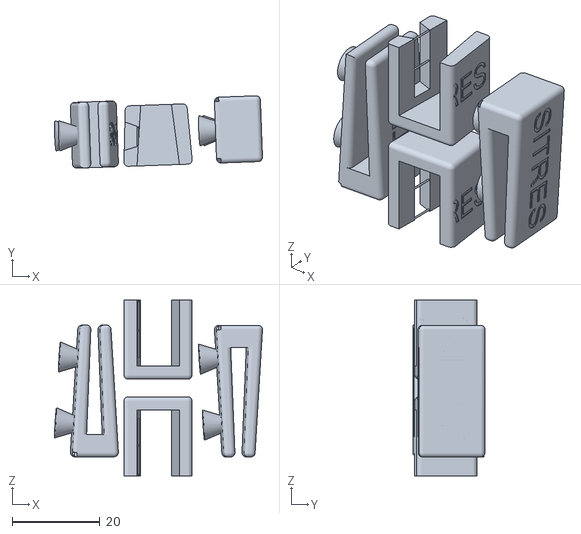
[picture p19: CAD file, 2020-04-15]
mascaras/SitresClips/Lentes.stl
47.4 x 16.5 x 40.0

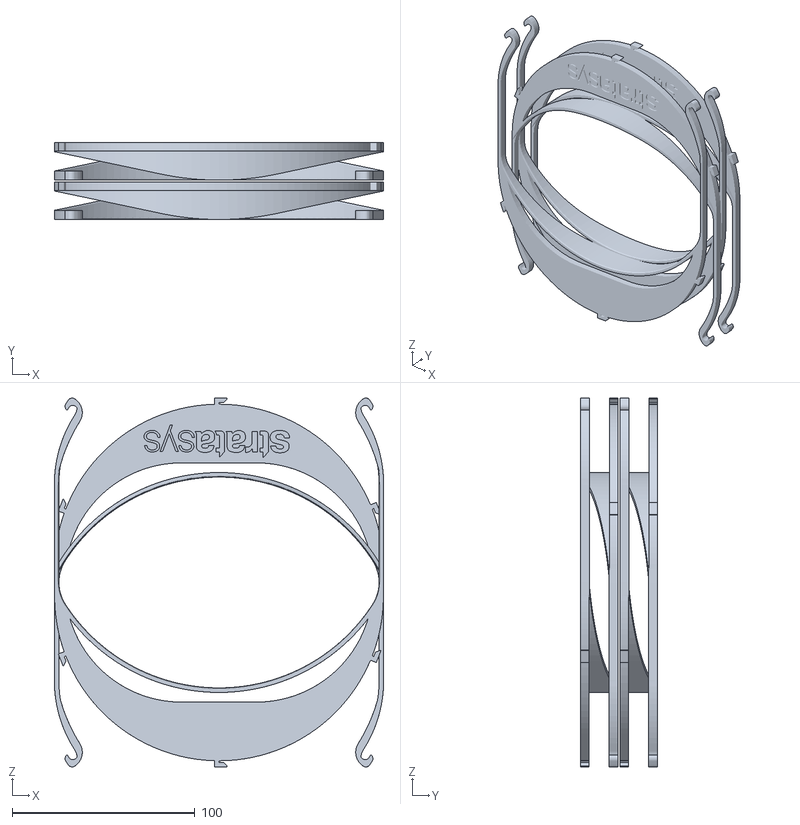
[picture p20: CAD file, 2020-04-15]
mascaras/Stratasys-Letter/Visor Manufacturing Package R3 2/Visor/4-Stack Visor Comfort Release.stl
180.0 x 42.0 x 201.7

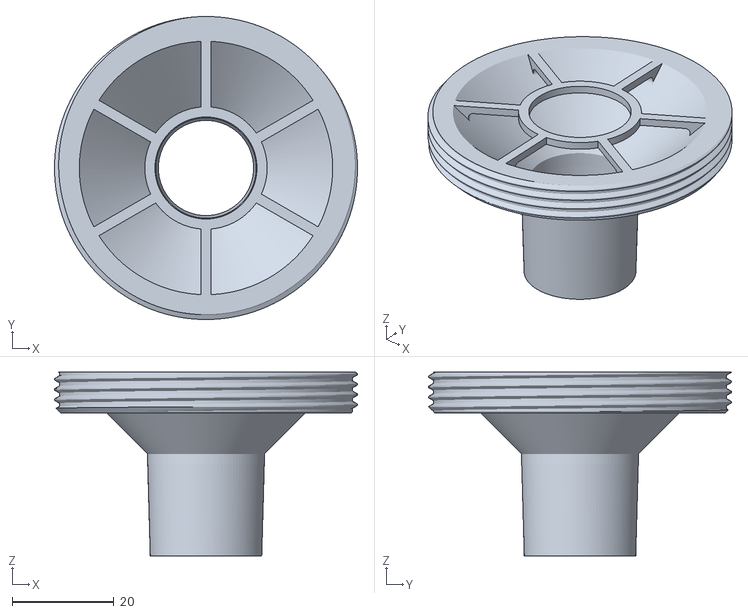
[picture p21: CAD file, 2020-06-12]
splitters/porta filtro macho v22.stl
59.4 x 59.4 x 36.0

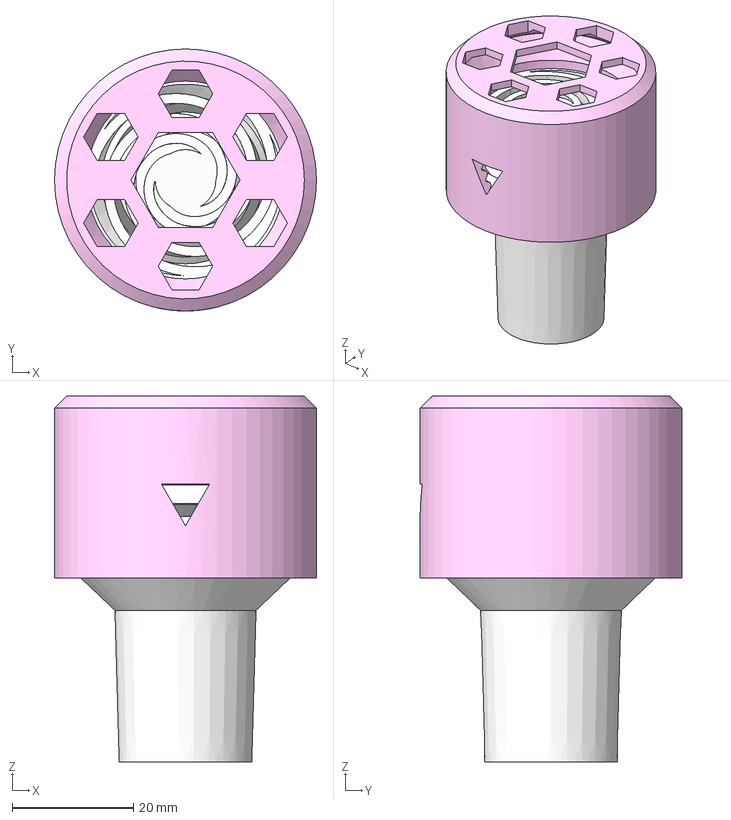
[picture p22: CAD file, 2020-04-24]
UNO/PEEP-Valve-ARDS_es/Peep_Completa.step
43.2 x 43.2 x 60.3 mm
BASE
SEAL
Stamper
SPRING
Cover

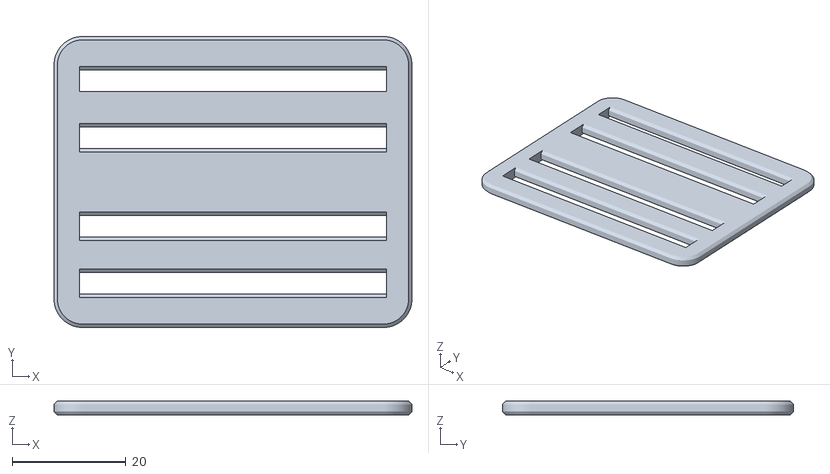
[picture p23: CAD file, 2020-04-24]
UNO/UNO-clip-big.stl
63.0 x 51.2 x 2.50

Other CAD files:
ventiladores/VentMex/stl/estructura/BasePrincipal-VentMex.STL
ventiladores/VentMex/stl/mecanico/SoporteEjePortaEncoder-VentMex.STL
ventiladores/VentMex/stl/oximetro/OximetroA-TOM.stl
mascaras/Stratasys-Letter/Visor Manufacturing Package R3 2/Visor/Visor No Logo.step
UNO/PEEP-Valve-ARDS_es/PEEP_Empaque.stl
UNO/PEEP-Valve-ARDS_es/PEEP_Estampar.stl
UNO/PEEP-Valve-ARDS_es/PEEP_Resorte.stl
UNO/PEEP-Valve-ARDS_es/PEEP_Tapa.stl
UNO/UNO-Y-sep.stl
UNO/UNO-acrilico-2mm.dxf
UNO/UNO-mask-v2.3.stl
mascaras/Stratasys-Letter/Visor Manufacturing Package R3 2/Shield/Shield R2.dxf
mascaras/Stratasys-Letter/Visor Manufacturing Package R3 2/Visor/2 side-by-side Visor Comfort Release.stl
mascaras/Stratasys-Letter/Visor Manufacturing Package R3 2/Visor/6-Stack side-by-side Visor.stl
mascaras/Stratasys-Letter/Visor Manufacturing Package R3 2/Visor/Visor SSYS Logo.stl
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

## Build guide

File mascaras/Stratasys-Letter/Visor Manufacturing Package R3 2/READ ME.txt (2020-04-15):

The Visor has been designed to comply with a standard 3-hole punch (4.25” spacing between holes), meaning you can 3-hole punch any clear plastic material and it will fit on the visor.

The Visor has been designed to also work on maker-level printers with PLA and no support removal required.

The fastener for the back of the Visor is a standard #33 rubber-band, however you should be able to use a zip tie, suture or other types of string to fasten the backend as needed. See: https://www.aerorubber.com/how-to-measure-a-rubber-band/ and http://www.industrialrubbergoods.com/rubber-bands.html

The processed files included are for various Stratasys machines.

Bill of Materials:
•	1 : Visor
•	1 : Shield
•	1 : #33 Rubber Band (or other fastener)

Assembly Instructions:
1.	Attach the shield to the visor by placing the holes on top of the three mounting points on the visor. 
2.	Rotate the visor counter-clockwise or the shield clockwise until the shield is in-place.
3.	Attach the #33 Rubber Band to the rear-side of the visor.
4.	Place the rear of the visor on the back of your head and slide the visor over your head until the front of the visor is on your forehead and the shield covers your face.

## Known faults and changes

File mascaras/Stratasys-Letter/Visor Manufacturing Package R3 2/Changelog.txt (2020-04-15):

(3/23/2020 4:00PM) R2 Release: Updated Shield Drawing

(3/26/2020 4:00PM) R3 Release: Created "Shield Materials.txt", created "Changelog.txt" and added the Material Matrix image.

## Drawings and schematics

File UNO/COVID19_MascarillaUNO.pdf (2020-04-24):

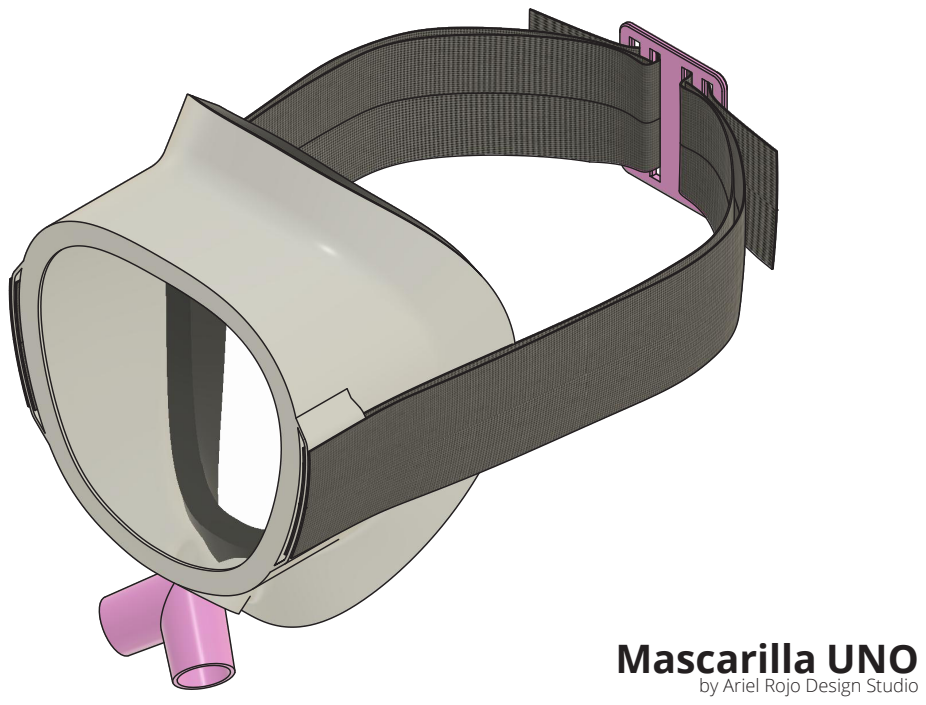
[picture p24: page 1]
Mascarilla UNO

by Ariel Rojo Design Studio

El diseño es una de las profesiones en donde se proyectan nuevas realidades, objetos y espacios en torno a los usuarios. Las necesidades y requerimientos del sector de la salud para atender a pacientes que enfrentan COVID-19 han surgido simultáneamente y en altas demandas. Para hacer frente a esto, la comunidad de hacedores y diseñadores de México se ha sumado al diseño y producción de piezas cortadas en láser o impresas en 3D que puedan ayudar en hospitales y hogares a los cuidados relacionados con este virus. Por medio de la organización TOM México, con Claudia Dorenbaum como coordinadora, las piezas se pueden fondear, administrar y distribuir entre los hospitales de la Ciudad de México.

Ariel Rojo, director de Ariel Rojo Design Studio (ARDS), bajo invitación del arquitecto Juan Carlos Baumgartner y Makers México, se unió a la comunidad de hacedores que se organizaban y pensaban cómo podían poner su creatividad y sus maquinas al servicio de la comunidad médica y social. Previendo el posible des-abasto de equipo médico que puede enfrentar la Ciudad de México por la alta densidad poblacional que presenta, inspirado en una pieza médica que se ha utilizado en otras ciudades y en la primera propuesta entregada por TOM México, Rojo rediseña un Splitter. Una pieza que ayuda a dividir el flujo de aire de un respirador artificial, de tal forma que puede ser compartido por dos pacientes. El rediseño de la pieza se hace para optimizar el flujo de aire, la resistencia mecánica y la facilidad de impresión 3D. Cabe mencionar, que esta herramienta no es la óptima, sin embargo en estos tiempos de crisis resulta una opción viable.

El estudio también diseñó mascarillas hospitalarias, para

# PROYECTO COVID-19

doctores y pacientes, con capacidad de conectarse a los distintos equipos médicos respiratorios y válvulas para respiradores. Ambas pensadas para ser open source y su producción en 3D entre la comunidad maker del mundo.

La mascarilla respiratoria de emergencia esta pensada como una herramienta para hacer frente a la problemática de la proliferación del Covid-19. Este proyecto nace a partir de una iniciativa de utilizar las mascarillas de buceo con adaptadores para equipo médico. No obstante la demanda de estos productos es mayor a los existentes. La forma general está basada para optimizar la capacidad de impresión 3D, y cuenta con distintas salidas y entradas para conectarse a distintos equipos médicos o para colocar filtros respiratorios.

En este proyecto participaron distintas personas:
Arquitecto Michel Rojkind enlace con el equipo médico especializado y Carsten Lemme como parte del equipo de ARDS quien colaboró en el desarrollo de estas piezas.

Ariel Rojo y sus colaboradores desarrollan estos productos, en una época en donde nos cuestionamos cómo debemos diseñar una mejor sociedad, pensando firmemente que el diseño debe ser social y colaborativo.

La mascarilla respiratoria de emergencia esta pensada como una herramienta para hacer frente a la problemática de la proliferación del Covid-19. La forma general está basada para optimizar la capacidad de impresión 3D,
y cuenta con distintas salidas y entradas para conectarse a distintos equipos médicos o para colocar filtros respiratorios.
A los centros de salud y fabricantes que lo requieran, podemos proporcionar más información y detalles, contactar a Makers México.

LOS ARCHIVOS DE LA MASCARILLA UNO SE PROPORCIONA “COMO ESTÁN”, SIN GARANTÍA DE NINGÚN TIPO. INCLUYENDO, PERO NO LIMITADO A, GARANTÍAS DE COMERCIALIZACIÓN. EN NINGÚN CASO ARIEL ROJO DESIGN STUDIO O PROPIETARIOS DE LOS DERECHOS DE AUTOR SERÁN RESPONSABLES DE NINGUNA RECLAMACIÓN, DAÑOS U OTRAS RESPONSABILIDADES, YA SEA EN UNA ACCIÓN DE CONTRATO, AGRAVIO O ASOCIADOS O CUALQUIER OTRO MOTIVO DERIVADAS DE, FUERA DE O EN CONEXIÓN, CON LA MASCARILLA UNO. SU USO U OTRO TIPO DE ACCIONES TENDRÁ QUE CONTAR CON LA APROBACIÓN DE PERSONAL MÉDICO ESPECIALIZADO.

# Mascarilla auxiliar respiratoria

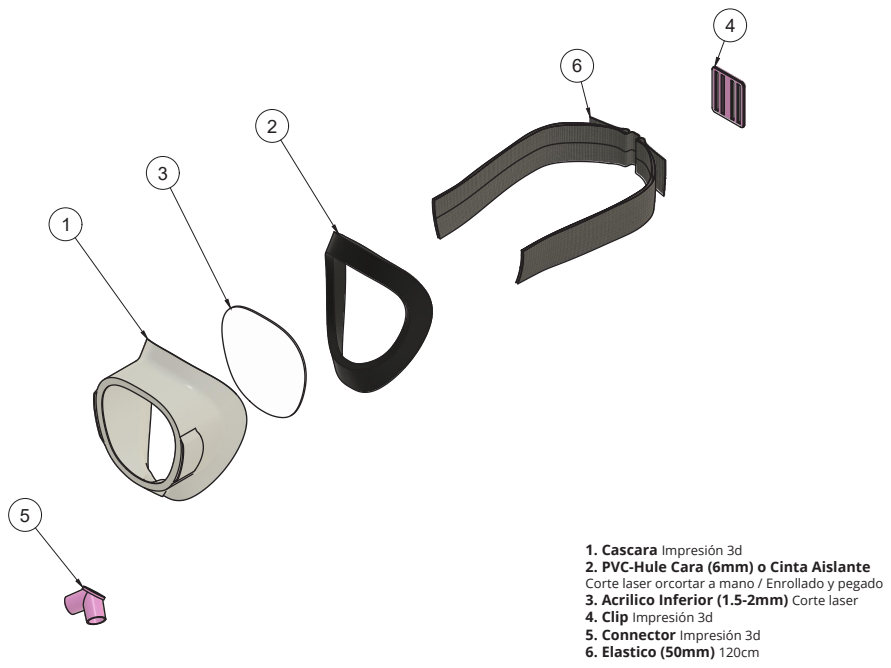
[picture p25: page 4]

1. Cascara Impresión 3d
2. PVC-Hule Cara (6mm) o Cinta Aislante
Corte laser orcortar a mano / Enrollado y pegado
3. Acrilico Inferior (1.5-2mm) Corte laser
5. Connector Impresión 3d

6 | 1 | Elastico_M2_DRAWING 4. Clip Impresión 3d
5 | 1 | Union y mascara 2
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

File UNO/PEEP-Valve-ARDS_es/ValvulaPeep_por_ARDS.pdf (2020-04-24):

# VÁLVULA-PEEP

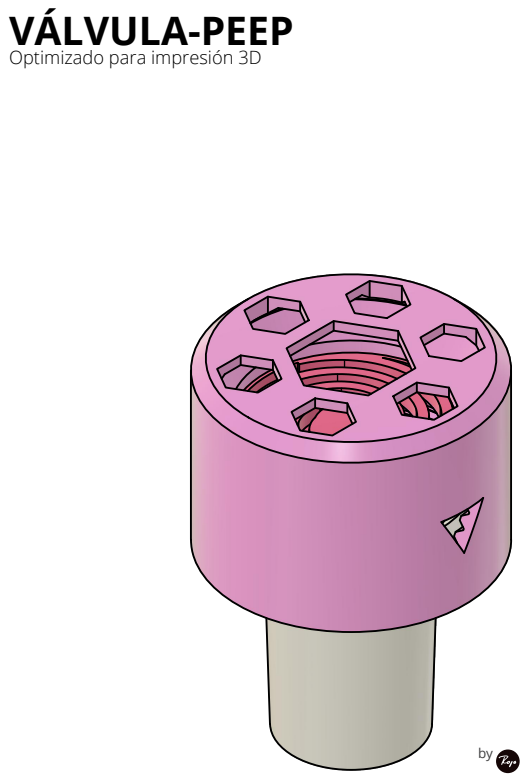
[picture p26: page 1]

Optimizado para impresión 3D

El diseño es una de las profesiones en donde se proyectan nuevas realidades, objetos y espacios en torno a los usuarios. Las necesidades y requerimientos del sector de la salud para atender a pacientes que enfrentan COVID-19 han surgido simultáneamente y en altas demandas. Para hacer frente a esto, la comunidad de hacedores y diseñadores de México se ha sumado al diseño y producción de piezas cortadas en láser o impresas en 3D que puedan ayudar en hospitales y hogares a los cuidados relacionados con este virus. Por medio de la organización TOM México, con Claudia Dorenbaum como coordinadora, las piezas se pueden fondear, administrar y distribuir entre los hospitales de la Ciudad de México.

Ariel Rojo, director de Ariel Rojo Design Studio (ARDS), bajo invitación del arquitecto Juan Carlos Baumgartner y Makers México, se unió a la comunidad de hacedores que se organizaban y pensaban cómo podían poner su creatividad y sus maquinas al servicio de la comunidad médica y social. Previendo el posible des-abasto de equipo médico que puede enfrentar la Ciudad de México por la alta densidad poblacional que presenta, inspirado en una pieza médica que se ha utilizado en otras ciudades y en la primera propuesta entregada por TOM México, Rojo rediseña un Splitter. Una pieza que ayuda a dividir el flujo de aire de un respirador artificial, de tal forma que puede ser compartido por dos pacientes. El rediseño de la pieza se hace para optimizar el flujo de aire, la resistencia mecánica y la facilidad de impresión 3D. Cabe mencionar, que esta herramienta no es la óptima, sin embargo en estos tiempos de crisis resulta una opción viable.

El estudio también diseñó mascarillas hospitalarias, para doctores y pacientes, con capacidad de conectarse a los distintos equipos médicos respiratorios y válvulas para respiradores. Ambas pensadas para ser open source y su producción en 3D entre la comunidad maker del mundo.

La mascarilla respiratoria de emergencia esta pensada como una herramienta para hacer frente a la problemática de la proliferación del COVID-19. Este proyecto nace a partir de una iniciativa de utilizar las mascarillas de buceo con adaptadores para equipo médico. No obstante la demanda de estos productos es mayor a los existentes. La forma general está basada para optimizar la capacidad de impresión 3D, y cuenta con distintas salidas y entradas para conectarse a distintos equipos médicos o para colocar filtros respiratorios.

En este proyecto participaron distintas personas:
Arquitecto Michel Rojkind enlace con el equipo médico especializado y Carsten Lemme como parte del equipo de ARDS quien colaboró en el desarrollo de estas piezas.

Para la válvula para respiradores, se hizo una optimización para impresión en 3D de un diseño open source que se encuentra en Thingiverse. El PandaPeep GEN2, creado por Dtextor, fue un gran punto de partida pero necesitaba adaptaciones para México. El despacho se encargó de diseñar estas adecuaciones a la pieza. La cual reconocemos es un ligero cambio al del autor original, a quien agradecemos la aportación, así como al sitio Thingiverse por difundir el conocimiento y poner a la mano estos diseños al servicios de la humanidad.

Ariel Rojo y sus colaboradores desarrollan estos productos, en una época en donde nos cuestionamos cómo debemos diseñar una mejor sociedad, pensando firmemente que el diseño debe ser social y colaborativo.

VÁLVULA-PEEPPOR ARIEL ROJO DESIGN STUDIO

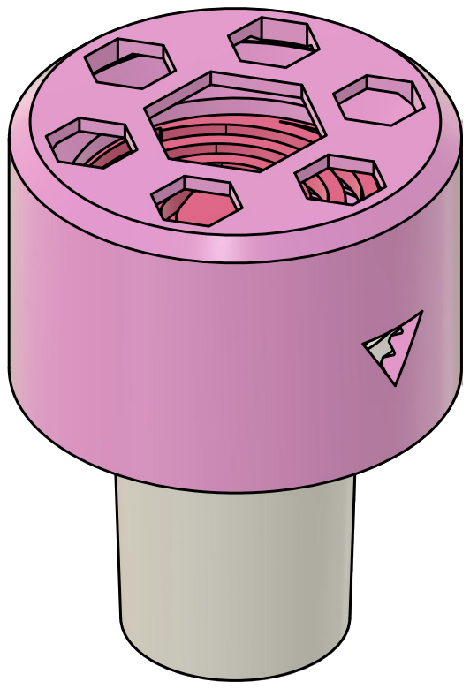
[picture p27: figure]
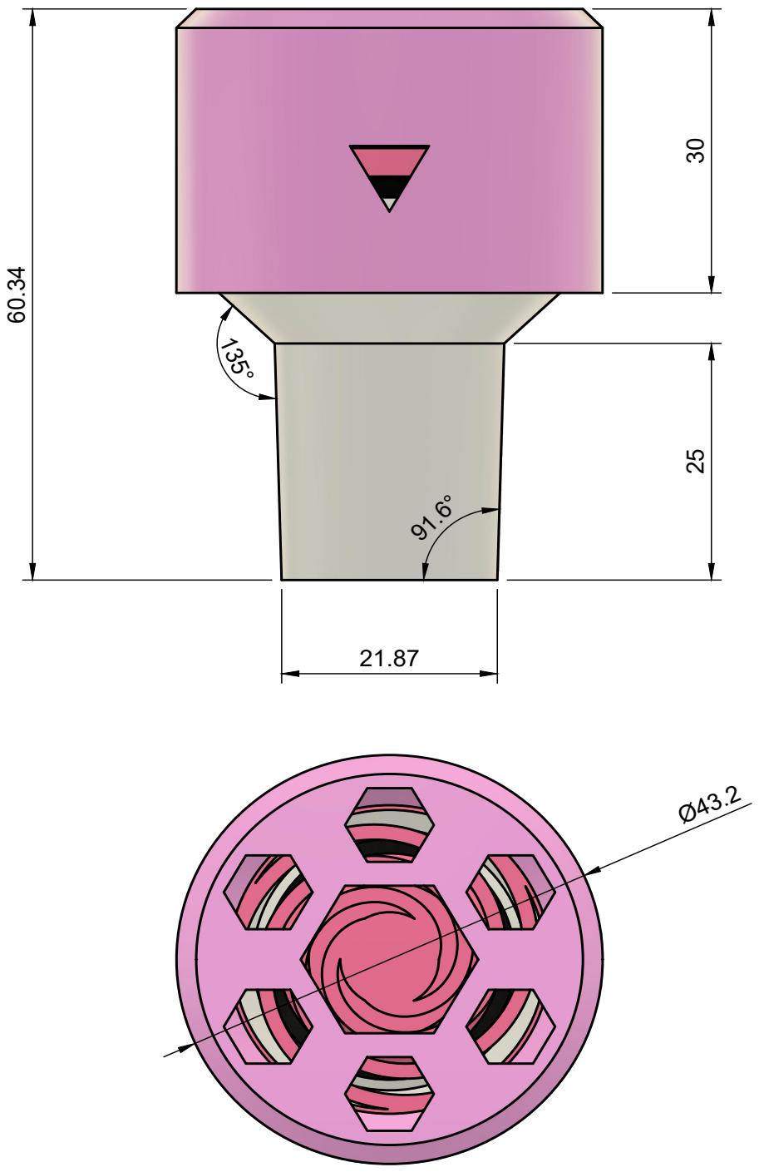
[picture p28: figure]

La válvula Peep es una reaptación del diseño open surce de la página Thingiverse. (https://www.thingiverse.com/thing:4250354/files) El PandaPeep GEN2, fue un gran punto de partida, sin embargo necesitaba una adaptación para ser compatible con los otros elementos de impresión 3D, relacionados con este proyecto, diseñados por ARDS.

Descarga los archivos open source aquí: MakersMexico.org

A los centros de salud y fabricantes que lo requieran, podemos proporcionar más información y detalles, contactar a Makers México.
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

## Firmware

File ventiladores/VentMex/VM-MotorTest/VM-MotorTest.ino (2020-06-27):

/*
   Demo for VentMex Motor Control and Calibration, using AccelStepper with NEMA-23
   200 Steps, 32 Microsteps
   Connect STEP, DIR as indicated
*/

#include <Arduino.h>
#include <Math.h>
#include <Streaming.h>
#include <AccelStepper.h>
#include <U8g2lib.h>
#include "VMPresion.h"
#include "VMFlujo.h"

// VARIAR ESTO PARA PRUEBAS asi no usamos pots para pruebas todavia
float RATEp           = 30.00;
float TDp             = 850.00;
float IEp             = 1.0;
//

// Motor steps per revolution. e 200 steps or 1.8 degrees/step
#define MOTOR_STEPS       200
#define FULL_TD_STEPS     77  // Cambiar a FS (Mitad de fsteps por el rodillo de Omer) 180 o 150 grados 950 ml
#define MICROSTEPS        32
#define STEP              6
#define PRESSURE          A0
#define IE                A4

// VentMex Shield Pinout
// Digital
#define ENABLE                    4 // Enable Motor PIN
#define DIR                       5 // Direction Motor PIN
#define STEP                      6 // Step Motor Pin
#define BUZZ                      7 // Buzzer PIN 
#define VENTILATOR                8 // Button On/Off Motors S4 VentMex
#define ENDSTOP                   9 // Button EndStop S3 VentMex
#define BUTTON_MOVE               10 // Button Move S2 VentMex
#define BUTTON_SELECT             11 // Button Select S1 VentMex
// Analog
#define PRESSURE                  A0
#define FLOW                      A1
#define JOYSTICK                  A2
#define RATE                      A3
#define IE                        A4
#define TD                        A5

// Graphs
int p_graph [100] = {};
int p_max = 40; // Presion Inspiratoria de 0 a 40 cmH2O
int p_min = -20;
char data[100];
int y_offset = 42;  
int x_offset = 65;


// Rangos para Potenciometros
const float BPM_MIN  = 5.0;
const float BPM_MAX  = 90.0;
const float VOL_MIN  = 20.0;
const float VOL_MAX  = 900.0;
const float IE_MIN = 1.0;
const float IE_MAX = 4.0;

// Setting de Seguridad
const float MAX_PRESSURE         = 40.0; // Trigger high pressure alarm
const float MIN_PLATEAU_PRESSURE =  5.0; // Trigger low pressure alarm
const float MAX_RESIST_PRESSURE  =  2.0; // Trigger high-resistance notification
const float MIN_TIDAL_PRESSURE   =  5.0; // Trigger no-tidal-pressure alarm


// Timing Settings
const float LOOP_PERIOD          = 0.03; // The period (s) of the control loop
const float HOLD_IN_DURATION     = 0.1;  // Duration (s) to pause after inhalation
const float MIN_PEEP_PAUSE       = 0.05; // Time (s) to pause after exhalation / before watching for an assisted inhalation
const float MAX_EX_DURATION      = 1.00; // Maximum exhale duration (s)

float tCycleTimer;            // Absolute time (s) at start of each breathing cycle
float tIn;                    // Calculated time (s) since tCycleTimer for end of IN_STATE
float tHoldIn;                // Calculated time (s) since tCycleTimer for end of HOLD_IN_STATE
float tEx;                    // Calculated time (s) since tCycleTimer for end of EX_STATE
float tPeriod;                // Calculated time (s) since tCycleTimer for end of cycle
float tPeriodActual;          // Actual time (s) since tCycleTimer at end of cycle (for logging)
float tLoopTimer;             // Absolute time (s) at start of each control loop iteration
float tLoopBuffer;            // Amount of time (s) left at end of each loop
float tins, tesp;             // Tiempos totales de Inspiracion y Espiracion

int tdSteps, inRPS, esRPS = 0;
int expiracion = 0;

float volume, pressure, flow, Pip, Peep, Plateau = 0.0;

int Pagina = 1;

VMPresion presion(A0);
VMFlujo flujo(A1);

AccelStepper stepper(AccelStepper::DRIVER, STEP, DIR);
U8G2_SSD1306_128X64_NONAME_F_HW_I2C pantalla(U8G2_R0, /* reset=*/ U8X8_PIN_NONE); //OLED Display I2C 0.96

// Returns the current time in seconds
inline float now()
{
  return millis() * 1e-3;
}

void calculaRespiracion() {

  tPeriod = 60.0 / RATEp;
  tHoldIn = tPeriod / (1 + IEp);
  tIn = tHoldIn - HOLD_IN_DURATION;
  //tEx = min(tHoldIn + MAX_EX_DURATION, tPeriod - MIN_PEEP_PAUSE); // Old Code para minimo de maxima exhalacion
  tEx = tPeriod - MIN_PEEP_PAUSE;

  //Calculamos Tiempos totales sin holds
  tins = tHoldIn;
  tesp = (tPeriod - tins);

  // Aqui calculamos tdSteps con algoritmo de AMBU (a calibrar)
  tdSteps = (int) flujo.volumenApasos(TDp);

  // Calc Step RPS para cada ciclo de Inspiracion y Expiracion
  inRPS = (tdSteps * 32.0) / tIn; // son RPS
  esRPS = (tdSteps * 32.0) / (tEx - tIn); // son RPS

  // Serial << "tPeriod: " << tPeriod << " tIn - tHoldIn - tEx - tEx + PeePPause= " << tIn << "-" << tHoldIn << "-" << tEx << "-" << (tEx + MIN_PEEP_PAUSE) << "\n";
  // Serial << "tins: " << tins << " tesp: " << tesp << " = " << (tins + tesp) << "\n" ;
  // Serial << "inRPS: " << inRPS << " esRPS: " << esRPS << " tdSteps:" << tdSteps*32 << "\n" ;
}

void cicloVentMex()
{
  presion.borra_pico();
  presion.lee();
  pressure = presion.get();

  expiracion = 1; // Icono Inspiracion
  tCycleTimer = now();

  stepper.setCurrentPosition(0);

  stepper.setMaxSpeed(-inRPS);
  stepper.setSpeed(-inRPS);

  sensorPantalla();

  while (true)
  {
    stepper.runSpeed();
    //if ((now() - tCycleTimer) >= tIn) // Llegue a tIn
    if (stepper.currentPosition() <= (-tdSteps * MICROSTEPS))
    {
      presion.lee();
      Pip = presion.pico();
      pressure = presion.get();
      flow = flujo.flujo(0.21);
      break;
    }
  }
  delay(HOLD_IN_DURATION);
  presion.lee();
  presion.pon_plateau(); // Pon Plateau (siempre como se lee presiones al principio de ciclo estamos), guarda
  flow = flujo.flujo(0.21);
  Plateau = round(presion.plateau());

  Serial << presion.get() << "\n";
  expiracion = 0; // Icono Espiracion
  stepper.setMaxSpeed(esRPS);
  stepper.setSpeed(esRPS);

  sensorPantalla();

  while (true)
  {
    stepper.runSpeed();
    //if ((now() - tCycleTimer) >= tEx) // Llegue a Ex final
    if (stepper.currentPosition() == 0)
    { // Llegamos a tEx + MIN_PEEP_WAIT lo minimo para medir Peep
      presion.lee();
      presion.pon_peep(); // Pon Peep (siempre como se lee presiones al principio de ciclo estamos)
      Peep = round(presion.peep());
      flow = flujo.flujo(0.21);
      Serial << presion.get() << "\n";
      break;
    }
  }
  delay(MIN_PEEP_PAUSE);
  presion.lee();
  pressure = presion.get();
  Pip = round(presion.pico());
  Plateau = round(presion.plateau());
  Peep = round(presion.peep());
  presion.borra_pico(); // pPIP se forza
  flow = flujo.flujo(0.21);
  //Serial << presion.get() << "\n";
  //Test (delay calc 80 ms)
  //float tR = (now() - tCycleTimer) - 0.08;
  //Serial << "Tiempo Real/Calc: " << tR << "/" << tPeriod << " (" << (tR - tPeriod) << ") " << ((tR * 100 / tPeriod) - 100) << "%\n";
}

void zigzag() // Zig Zag Prueba Basica sin mediciones ni carga ni nada
{

  expiracion = 1; // Icono Inspiracion
  tCycleTimer = now();

  stepper.setCurrentPosition(0);
  stepper.setMaxSpeed(-inRPS);
  stepper.setSpeed(-inRPS);

  sensorPantalla();
  while (true)
  {
    stepper.runSpeed();
    if (stepper.currentPosition() <= (-tdSteps * MICROSTEPS)) break;
  }

  Serial << (now() - tCycleTimer) << ":" << tIn << "(" << ((now() - tCycleTimer) - tIn) << ")\n";

  expiracion = 0; // Icono Espiracion
  tCycleTimer = now();
  stepper.setMaxSpeed(esRPS);
  stepper.setSpeed(esRPS);

  sensorPantalla();
  while (true)
  {
    stepper.runSpeed(); // Esto avanza el Loop
    if (stepper.currentPosition() == 0) break;
  }

  Serial << (now() - tCycleTimer) << ":" << (tEx - tIn) << "(" << ((now() - tCycleTimer) - (tEx - tIn)) << ")\n\n";

}

void homeMotor()
{
  Serial << "Homing ...\n";
  stepper.setMaxSpeed(3200);  // 1/2 velocidad para homing
  stepper.setAcceleration(42666); // Aceleracion rapida siempre
  stepper.moveTo(64000);  // 100 vueltas aprox max encontrar switch

  while (true)
  {
    stepper.run();
    if (digitalRead(ENDSTOP) == LOW)
    {
      //Serial << "Homed ...\n";
      stepper.setCurrentPosition(0);
      stepper.stop();
      break;
    }
    if (stepper.distanceToGo() == 0)
    {
      //Serial << "Not Homed, Error! ...\n";
      initPantalla("ERROR NOT HOME");
      stepper.stop();
    }
  }
}

void leeControles()
{
  IEp   = map(analogRead(IE), 5, 1020, IE_MIN, IE_MAX);     // IE de 1:1 a 1:4 por pacientes de Covid-19
  RATEp = map(analogRead(RATE), 5, 1020, BPM_MIN, BPM_MAX); // 5 a 30 BPM
  TDp   = map(analogRead(TD), 5, 1020, VOL_MIN, VOL_MAX);   // 100 a 1000 cmH2O - vs 250 to 600
  // Overrride Tests
  //TDp = 850.00;
  //IEp = 1.00;
}

void logicaPantalla()
{
  int joy = analogRead(JOYSTICK);
  if (joy >= 560)
  {
    Pagina++;
    if (Pagina == 5) Pagina = 1;
  }

  if (joy <= 480)
  {
    Pagina--;
    if (Pagina == 0) Pagina = 4;
  }

  if (digitalRead(BUTTON_SELECT) == 0 && (joy <= 480 || joy >= 560)) {
    //tomDelay(100);
    //setupTVM();
  }

  switch (Pagina)
  {
    case 1:
      {
        todoPantalla();
        break;
      }
    case 2:
      {
        presionGrafica();
        break;
      }
    case 3:
      {
        presionPantalla();
        break;
      }
    case 4:
      {
        flujoPantalla();
        break;
      }
  }
}

void sensorPantalla()
{
  char buff[6];

  pantalla.setDrawColor(0);
  pantalla.drawBox(0, 0, 128, 16);
  pantalla.setDrawColor(1);

  pantalla.setFont(u8g2_font_8x13B_mr);
  pantalla.setCursor(-1, 13);
  pantalla.print("1:");
  pantalla.print(dtostrf(IEp, 1, 0, buff));
  pantalla.drawLine(26, 0, 26, 16); // Vertical Line
  pantalla.setFont(u8g2_font_6x12_tf);
  pantalla.setCursor(30, 13);
  pantalla.print(dtostrf(tIn, 1, 1, buff));
  pantalla.print("/");
  pantalla.print(dtostrf((tEx - tIn), 1, 1, buff));
  pantalla.print("s");
  pantalla.setFont(u8g2_font_t0_13_te);
  pantalla.setCursor(88, 13);
  pantalla.print(dtostrf(RATEp, 3, 0, buff)); // Ritmo Respiratorio
  pantalla.drawLine(0, 16, 128, 16); // Horizontal Line

  if (expiracion == 1) //  exhala
  {
    // pantalla.setFont(u8g2_font_open_iconic_human_2x_t);
    pantalla.setFont(u8g2_font_cursor_tf);
    pantalla.setCursor(120, 8);
    pantalla.print(char(57)); // Pulmon @1n
  } else {
    // pantalla.setFont(u8g2_font_open_iconic_human_1x_t);
    pantalla.setFont(u8g2_font_cursor_tf);
    pantalla.setCursor(120, 8); // RIGHT
    pantalla.print(char(56)); // Pulmon @2b
  }
  pantalla.setFont(u8g2_font_6x12_tf); // tf tr tn te

  pantalla.sendBuffer();

  p_graph[64] = (pressure) * (y_offset - 20) / p_max;

  for (int x = 0; x < 64; x++) 
  {
    p_graph[x] = p_graph[x + 1];
  }

}

void todoPantalla() {

  char buff[6];

  pantalla.setDrawColor(0);
  pantalla.drawBox(0, 17, 128, 64);
  pantalla.setDrawColor(1);

  pantalla.drawLine(62, 16, 62, 64); // Vertical Line
  pantalla.drawLine(97, 16, 97, 48); // Vertical Line
  pantalla.drawLine(0, 48, 128, 48); // Horizontal Line
  int y = 30;
  pantalla.setFont(u8g2_font_6x12_tf); // tf tr tn te
  pantalla.setCursor(0, y);
  pantalla.print(" Flujo/Vt  ");
  pantalla.print(dtostrf(flow, 3, 0, buff));
  pantalla.print("   ");
  pantalla.print(dtostrf(TDp, 3, 0, buff));
  pantalla.setCursor(0, y + 13);
  pantalla.print(" SpO²/FiO²  ");
  pantalla.print(dtostrf(21, 3, 0 , buff)); //SpO2
  pantalla.print("   ");
  pantalla.print(dtostrf(21, 3, 0 , buff)); // FiO2
  pantalla.setCursor(0, y + 30);
  pantalla.print(" P:Pep/PIn ");
  pantalla.print(dtostrf(presion.get(), 3, 0 , buff));
  pantalla.print(":");
  //pantalla.setCursor(75, y + 30);
  pantalla.print(dtostrf(Peep, 2, 0, buff));
  pantalla.print("/");
  pantalla.print(dtostrf(Pip, 2, 0 , buff));
  pantalla.sendBuffer();
}
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

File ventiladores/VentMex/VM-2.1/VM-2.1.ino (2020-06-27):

/**
   TOM VentMex Emergency Ventilator Controller

   TOM Makers - Mexico

   Copyright (c) 2020 makersmexico.org

   Creative Commons Attribution-NonCommercial 4.0 International (CC BY-NC 4.0)
   This is a human-readable summary of (and not a substitute for) the license. Disclaimer.
   You are free to:
        Share — copy and redistribute the material in any medium or format
        Adapt — remix, transform, and build upon the material
   The licensor cannot revoke these freedoms as long as you follow the license terms.

   Under the following terms:
   Attribution — You must give appropriate credit, provide a link to the license, and indicate if changes were made.
   You may do so in any reasonable manner, but not in any way that suggests the licensor endorses you or your use.

   NonCommercial — You may not use the material for commercial purposes.

   No additional restrictions — You may not apply legal terms or technological measures that legally restrict others from doing anything the license permits.
   Notices:
   You do not have to comply with the license for elements of the material in the public domain or where your use is permitted by an applicable exception or limitation.
   No warranties are given. The license may not give you all of the permissions necessary for your intended use. For example, other rights such as publicity, privacy,
   or moral rights may limit how you use the material.

   Marvin Nahmias - on UxD, systems, electronics and software, marvin@tomglobal.org
   Omer Sebastian Larranaga - on mechanotronics, electronics, 3d Design, sensors and first build tests

 *** Referenced State machine logic, constants and timing graphs taken from MIT https://e-vent.mit.edu/ and all their licencing apply accordingly.

   MIT License:

   Copyright (c) 2020 MIT

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
 *** Referenced Mechanical Original Design ONLY from Formon Ventcore-health https://www.ventcore.health/ and all their licencing apply accordingly
   @ https://www.ventcore.health/index.php/terms-of-use/

  MEXICO COFEPRIS MONITOREO Y PARAMS:

  -Volumen corriente o tidal
    2 mL a 2000 mL o mayor, para ventilador adulto-pediátrico-neonatal.
    Al menos 25 a 50 mL en el límite inferior y 2000 mL o mayor en el límite superior para el ventilador adulto-pediátrico.
    2 mL a 2000 mL para el ventilador neonatal.
  -Frecuencia respiratoria
    Rango de 0 a 150 respiraciones por minuto.
  -Presión positiva aérea continua (CPAP/PEEP)
    Rango de 0 a 20 cm H20.
  -Presión soporte (NO APLICA)
    Rango de 0 a 45 cm H20.
  -Fracción inspirada de oxígeno (FiO2) (Vendra del Oximetro)
    Entre 21 y 100%.
  -Tiempos inspiratorios y espiratorios
    Al menos 0.1 seg y 10 seg respectivamente.
  -Relación entre tiempo inspiratorio y el tiempo espiratorio
    De 1:1 a 1:3
  -Flujo inspiratorio
    Rango de 0 a 150 L/min.
  -Presión inspiratoria
    Rango de 0 a 80 cm de H20.

  MEXICO COFEPRIS ALARMAS:
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

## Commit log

2020-04-24 Creacion de UNO Mask, estructura
    [PEEP_Base.stl, PEEP_Empaque.stl, PEEP_Estampar.stl, PEEP_Resorte.stl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]
2020-04-24 Restructura de directorios y archivos
    [2 side-by-side Visor Comfort Release.stl, 2-Stack Visor Comfort Release.stl, 4-Stack Visor Comfort Release.stl, 6-Stack side-by-side Visor.stl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]
2020-06-12 Porta Filtro : HEPA ARDS
    [porta filtro hembra v22.stl, porta filtro macho v22.stl]
2020-06-12 new software, libraries, stl, files and structure.
    [BasePrincipal-VentMex.STL, OximetroA-TOM.stl, OximetroB-TOM.stl, RodilloConRodamiento-VentMex.STL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]
2020-06-27 CicloVentMex Redone with Sensors Calibrated
    [3DP_bvmholder_1a.STL, 3DP_bvmholder_1b.STL, 3DP_bvmholder_2a.STL, 3DP_bvmholder_2b.STL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]
2020-06-27 Resultado de 200 mediciones y generación de curvas de calibración. Omer y Co.
    [VM-Calib-Sensores.xlsx]
